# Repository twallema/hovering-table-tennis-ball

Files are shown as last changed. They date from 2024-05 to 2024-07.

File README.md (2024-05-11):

# Control Theory Hands-on Practical

## Hovering a table tennis ball at a fixed height

Dr. Tijs W. Alleman, Daniel Illana, Dr. Gauthier Vanhaelewyn

Correspondence: tijs.alleman@ugent.be 

BIOMATH, Department of Data Analysis and Mathematical Modelling, Ghent University, Coupure Links 653, Ghent, 9000, Belgium

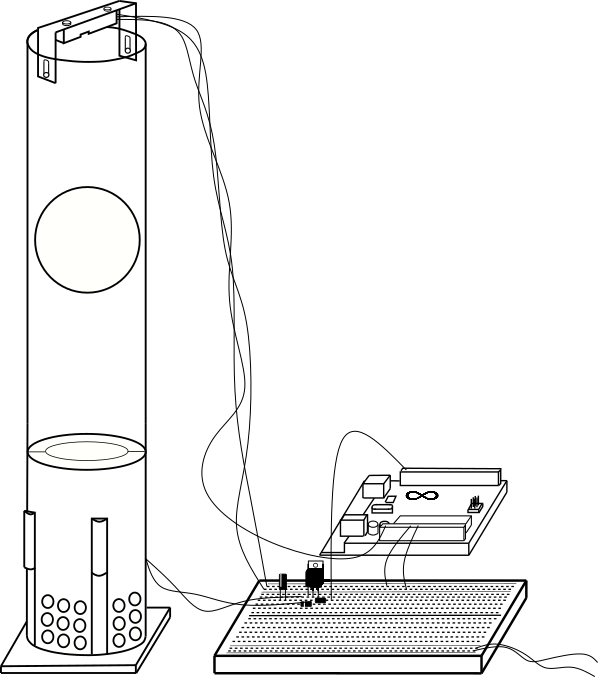
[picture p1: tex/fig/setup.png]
setup


### Aim

In this practical, we turn control theory into practice by hovering a table tennis ball at a fixed height in a transparent tube. We use an Arduino Uno to build a closed loop feedback controller. We measure the ball’s height using an infrared distance sensor at the top of the tube, which we the use to control a fan at the bottom of the tube. First, we study the setup’s open-loop behavior and gather response data to calibrate a mathematical model. We then use Matlab’s Simulink environment to perform an in-silico tuning of several closed-loop feedback controllers, such as the Proportional-Integral-Derivative (PID) controller and Linear-Quadratic Regulator (LQR) state feedback controller. Finally, the performance of the tuned controllers is examined and compared using the experimental setup. This setup serves as an intuitive and visual test bed for the closed-loop feedback controllers introduced in the theoretical course. Our aim is to introduce students to the use of electronics, the unfortunate reality of noisy sensors and dead time, along with their implications on closed-loop stability, the application of control theory to non-linear systems, and to the use of mathematical modeling to support the in-silico design of a suitable controller.

### Getting started

All relevant information is included in the practical notes. This repository contains all LaTex, Matlab, and Wolfram Mathematica code needed to replicate the results shown in the practical notes.

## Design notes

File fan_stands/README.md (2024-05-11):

# Fan stands

+ `FUFTICAILV80G0N.stl`: Original fan stand, retrieved from https://www.instructables.com/Float-a-Ping-Pong-Ball-at-Will/

+ `fan_stand_short.stl`: Modified fan stand. Modification of `FUFTICAILV80G0N.stl` so transparent polycarbonate tube can fit inside the fan stand. By Ben de Saveur. Has not been 3D printed and tested (11/05/2024).

+ `fan_stand_long.stl`: Modified fan stand. Elongation of `fan_stand_short.stl`, in order to have more distance between the fan and the ball, which will likely minimise lift-off dead time.  By Ben de Saveur. Has not been 3D printed and tested (11/05/2024).

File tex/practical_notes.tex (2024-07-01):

\documentclass[10pt,twoside,openright]{article}

%---------------------------------------------------------------------------
%List of packages with theid respective use, you can uncomment if not used
%---------------------------------------------------------------------------

%--------------layout of the document--------------
% this package is used to get a wider A4 paper
\usepackage{a4wide}
% these packages are used to produce nicer captions
\usepackage[font={small},labelfont={bf,sf},width=0.8\textwidth, singlelinecheck=false]{caption}
%\usepackage[font={small},labelfont={bf,sf},hang,singlelinecheck=false]{caption}
% use the titlesec package to change the section 
\usepackage[calcwidth,newparttoc]{titlesec}
% use the titletoc package to change the toc
\usepackage{titletoc}
% hyperrefs used in the produced pdf file
\usepackage[a4paper,plainpages=false]{hyperref}
% this package is used for colored text
\usepackage{xcolor}
%\usepackage[cmyk]{xcolor}
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
%http://anthony.liekens.net/index.php/LaTeX/SubscriptAndSuperscriptInTextMode
\newcommand{\superscript}[1]{\ensuremath{^{\textrm{#1}}}} 
\newcommand{\subscript}[1]{\ensuremath{_{\textrm{#1}}}}
% new commands to create nicer sub and superscripts in math mode
\newcommand{\sms}[1]{\mbox{\tiny{#1}}}
\newcommand{\lss}[1]{_{\mbox{\tiny{#1}}}}
\newcommand{\uss}[1]{^{\mbox{\tiny{#1}}}}

%---------------------------------------------------------------------------
% Short version commando to introduce figures. 
%---------------------------------------------------------------------------
%\mijnfiguur[H]{width=5cm}{bestandsnaam}{Het bijschrift bij deze figuur}{label}
\newcommand{\mijnfiguur}[5][ht]{            % Het eerste argument is standaar `ht'.
    \begin{figure}[#1]                      % Beginnen van de figure omgeving
        \begin{center}                      % Beginnen van de center omgeving
                    % Het eigenlijk invoegen van de figuur (2: opties, 3: bestandsnaam)
        \end{center}
        \caption{#4\label{#5}}          % Het bijschrift (argument 4) en het label (argument 3)
    \end{figure}
    }

%-----------------------------------------------------------------------------------------
% PDF properties (you only see this as document properties (metadata) of your pdf-document
%-----------------------------------------------------------------------------------------
\hypersetup{
    pdfauthor = {Your name},
    pdftitle = {Your title},
    pdfkeywords = {some relevant keywords}}

\setcounter{MaxMatrixCols}{20}

\usepackage{tcolorbox}
\usepackage{lipsum}
\usepackage{verbatim}

%path to graphics
\graphicspath{{fig/}}

%-------------------------------
% Opgave / Oplossing environment
%-------------------------------

\usepackage[framemethod=TikZ]{mdframed}
\mdfdefinestyle{warning}{%
	linecolor=white,
	align=center,
	roundcorner=3pt,
	innertopmargin=6pt,
	innerbottommargin=5pt,
	innerrightmargin=10pt,
	innerleftmargin=10pt,
	backgroundcolor=black!12,
	skipabove=0.4\baselineskip
}

\newcounter{opgave}[section]\setcounter{opgave}{0}
\renewcommand{\theopgave}{\arabic{section}.\arabic{opgave}}
\newenvironment{opgave}[2][]{%
	\refstepcounter{opgave}
	\label{#2}
	\mdfsetup{%
		frametitle={%
			\tikz[baseline=(current bounding box.east),outer sep=0pt]
			\node[anchor=east,rectangle,fill=gray!40]
			{\strut Exercise~\theopgave:~#1};}%
	}
	\mdfsetup{%
		innertopmargin=10pt,linecolor=white!30,%
		linewidth=0pt,topline=true,%
		frametitleaboveskip=\dimexpr-\ht\strutbox\relax%
	}

	\begin{mdframed}[]\relax}{%
\end{mdframed}}

\newenvironment{oplossing}[2][]{%
	\mdfsetup{%
		frametitle={%
			\tikz[baseline=(current bounding box.east),outer sep=0pt]
			\node[anchor=east,rectangle,fill=gray!20]
			{\strut Solution};}%
	}
	\mdfsetup{%
		innertopmargin=10pt,linecolor=white!30,
		linewidth=0pt,topline=true,%
		frametitleaboveskip=\dimexpr-\ht\strutbox\relax%
	}
	
	\begin{mdframed}[]\relax}{%
\end{mdframed}}

% ------------------
% Leeg vak
% ------------------

\newlength{\lvaklength}

\newcommand{\leegvak}[2]{\noindent\framebox[#1]{\parbox{#1}{\vspace{#2}}}}
\newcommand{\leegvakf}[1]{
\setlength{\lvaklength}{0cm}
\addtolength{\lvaklength}{0.925\textwidth}
%\addtolength{\lvaklength}{-\leftmargin}
\leegvak{\lvaklength}{#1}
}

\newcommand{\leegvakg}[1]{
\setlength{\lvaklength}{0cm}
\addtolength{\lvaklength}{0.875\textwidth}
%\addtolength{\lvaklength}{-\leftmargin}
\leegvak{\lvaklength}{#1}
}

\newcommand{\solbox}[2]{
\noindent\framebox[0.925\textwidth]{
\parbox{#1}{\vspace{#1}}
\begin{minipage}[c][#1][c]{0.925\textwidth}
	\centering
	#2
\end{minipage}
}}

%---------------------------------------------------------------------------
%---------------------------------------------------------------------------
% The actual document starts here
%---------------------------------------------------------------------------
%---------------------------------------------------------------------------
\begin{document}

\title{%
  Control Theory Hands-on Practical \\
  \Large Hovering a table tennis ball at a fixed height}
  
\author{Dr.~Tijs W. Alleman$^{1,2,*}$, Daniel Illana$^{1}$, Dr.~Gauthier Vanhaelewyn$^{1}$, Dr.~Elena Torfs$^{1,3}$}
\maketitle

$^*$Correspondence: \url{tijs.alleman@ugent.be} \\
$^1$BIOMATH, Department of Data Analysis and Mathematical Modelling, Ghent University\\
$^2$Infectious Disease Dynamics Group, Department of International Health, Johns Hopkins University Bloomberg School of Public Health\\
$^3$modelEAU, Department of Civil Engineering and Water Engineering, Universit\'e Laval\\
Available on GitHub: \url{https://github.com/twallema/hovering-table-tennis-ball}\\

\begin{center}

\end{center}

\paragraph{Aim} In this practical, we turn control theory into practice by hovering a table tennis ball at a fixed height in a transparent tube. We use an Arduino Uno to build a closed loop feedback controller. We measure the ball's height using an infrared distance sensor at the top of the tube, which we the use to control a fan at the bottom of the tube. First, we study the setup's open-loop behavior and gather response data to calibrate a mathematical model. We then use Matlab's Simulink environment to perform an in-silico tuning of several closed-loop feedback controllers, such as the Proportional-Integral-Derivative (PID) controller and Linear-Quadratic Regulator (LQR) state feedback controller. Finally, the performance of the tuned controllers is examined and compared using the experimental setup. This setup serves as an intuitive and visual test bed for the closed-loop feedback controllers introduced in the theoretical course. Our aim is to introduce students to the use of electronics, the unfortunate reality of noisy sensors and dead time, along with their implications on closed-loop stability, the application of control theory to non-linear systems, and to the use of mathematical modeling to support the in-silico design of a suitable controller.

\setcounter{tocdepth}{2}
\tableofcontents

\clearpage
\section{Introduction}

\subsection{Electronics}

To build the practical setup, we first need to familiarise ourselves with the bread and butter of electronics: the resistor, capacitor, diode and transistor. In this short intro we use the hydraulic circuit analogy, to explain some basic concepts. In this analogy, an electrical circuit is thought to be a hydraulic circuit consisting of pipes, valves, pumps, etc. Charge is represented by the water amount, voltage is represented by the water pressure, and current is represented by the water flow.

\paragraph{Resistor}
As the name implies, resistors add resistance to the circuit and reduce the flow of electrical current. In the hydraulical circuit analogy a resistance is represented by a throttling valve, or alternatively, as rocks in a river, hindering the flow of water. Resistors are typically represented as a pointy squiggle with a value next to it (Fig.~\ref{fig:resistor}). In electronic devices, resistors are used to avoid damage resulting from high currents. When building an electronic circuit, it is paramount to check the amount of current flowing through each analog component by using Ohm's law,
\begin{equation}
I = \frac{V}{R},
\label{eqn:Ohms law}
\end{equation}
where V is voltage in Volt (V), I is the electric current in Amps (A) and R is the resistance in Ohms ($\Omega$). Most electronic components, f.i. an LED, have little internal resistance. When applying even the smallest voltage directly to an LED, the LED will light up briefly and then shutdown forever. Generally speaking, overloading electronic circuits by mistake is common and not very dangerous. \textbf{In any case, when noticing the characteristic smell of a shortcircuit (a combination of ozone and burnt plastic) during this practical, please pull out the wall plug immediately!} During this practical we will use a 2.2 $k\Omega$ resistor to limit the current of a voltage sent from the Arduino Uno to a transistor.
\mijnfiguur[h!]{width=6cm}{resistor.jpg}{(upper) real life resistor. (lower) schematic representation of a transistor.}{fig:resistor}

\paragraph{Capacitor}
A capacitor is a component that stores electricity and then discharges it into the circuit when there is a drop in current. You can think of a capacitor as a water storage tank that releases water when there is a drought to ensure a steady stream. Therefore, capacitors are typically used to filter a noisy current. Further, capacitors are preferred over batteries in applications that require a rapid discharge, such as in a defibrillator. The values that you will typically encounter in most capacitors are measured in picofarad (pF), nanofarad (nF), and microfarad ($\mu F$). The most commonly encountered types of capacitors are ceramic disc capacitors that look like tiny M\&Ms with two wires sticking out of them and electrolytic capacitors that look more like small cylindrical tubes with two wires coming out the bottom (Fig.~\ref{fig:capacitor}). The main difference is that ceramic disc capacitors are non-polarized, meaning that electricity can pass through them no matter how they are inserted in the circuit. Opposed, electrolytic capacitors are polarized, meaning one leg needs to be connected to the ground side of the circuit and the other leg must be connected to power. For this practical we will be using a 22 $\mu F$ electrolytic capacitor as an analog filter for the power supply of the IR proximity sensor. \textbf{Because the provided capacitor is electrolytic, please make sure you respect its polarity.}

\mijnfiguur[h!]{width=7cm}{capacitor.jpg}{(left) real life ceramic capacitor and schematic representation (right) real life electrolytic capacitor and schematic representation.}{fig:capacitor}

%bron figuren: https://www.instructables.com/id/Basic-Electronics/

\paragraph{Diode}
A diode only allows electrical current to pass through them in one direction, its hydraulic analogy is a non-return valve. Diodes are useful to prevent electricity from flowing in the wrong direction. When the voltage applied to an electric DC motor is abruptly switched off, the fan will keep spinning for a short while. As such, the motor will act as a generator of current until its blades come to a standstill. Charge will build up on what was the negative terminal of the motor and this charge will want 'a way out'. Adding a diode in parallel with the motor provides a path for dissipation of stored energy when the voltage is cut. Similar to the electrolytic capacitor, the diode is polarised and the ring found on one end of the diode indicates the side of the diode which connects to ground. \textbf{When building the setup, please mind that the ring on the diode points in the right direction (Fig.~\ref{fig:fritzing}).}

\mijnfiguur[h!]{width=6cm}{diode.jpg}{(upper) real life diode (lower) schematic representation of a diode.}{fig:diode}
%\mijnfiguur[h!]{width=5cm}{flybackDiode.png}{The flyback diode allows charge to dissipate without arcing across the switch (analog component), or without flowing back to ground through the +5 V voltage supply.}{fig:flybackDiode}

\paragraph{Transistor} A transistor can act as a switch or gate for electronic signals, opening and closing many times per second. It typically has three pins: the base, emitter and collector pins (Fig.~\ref{fig:transistor}). A transistor uses a small electrical current at its base pin to control the current passing between its collector and emitter pins. The amount of current allowed to pass between the collector and emitter pins is proportional to the voltage being applied at the base pin. A transistor is therefore a good way of controlling a high voltage/high current circuit (fan motor, 12 VDC) using a low voltage/low current signal (Arduino, 5 VDC). An (inperfect) hydraulic analogy for a transistor is an adjustable valve. Passing current through a transistor costs energy and therefore observing a voltage drop of 1 V over a transistor is common. This energy is dissipated in heat so \textbf{transistors heat up to well over 100 \textdegree C under load. Never touch your transistor while operating the setup!}\\

\mijnfiguur[h!]{width=6cm}{BD537.jpg}{BD537 transistor used to control the fan's motor.}{fig:transistor}

%\begin{tcolorbox}[colback=white,colframe=black,title=\textbf{Takeaway lessons}]
%\begin{itemize}
%\itemsep0em 
%\item A limited number of analog components can be arranged to fulfill specific tasks. This is accomplished by designing the circuit so that the right current is provided to the right component.
%\item Analog components can be combined with programmable microcontrollers so that the amount of current flowing through each analog component can vary/be controlled. This allows to build more complex/interactive electronics.
%\end{itemize}
%\end{tcolorbox}

%bron: https://www.arduino.cc/en/guide/introduction, Arduino voor Dummies (John Nussey)

\subsection{The Arduino Uno Rev 3, its components and signals}

Using only resistors, capacitors, diodes and transistors, it is possible to build simple electronic devices that do a specific job, such as an egg timer or a security buzzer that goes off when you keep the fridge open too long. The behavior of such circuits is solely based on the chemical properties of the components, which need to be computed beforehand to make sure that the right amount of current is flowing through the right components. This makes these simple devices very good at their specific job, but they're limited in what they can do. The microcontroller, a tiny computer present on the Arduino Uno can be used can be used in conjunction with the aforementioned analog circuitry to allow for more advanced behavior. The amount of current flowing through the analog components is now variable and controlled, rather than constant and computed beforehand.\\

Arduino is an open-source electronics platform based on easy-to-use hardware and software. The Arduino hardware consists of a small circuit board containing a microcontroller chip and several connections (Fig.~\ref{fig:ARDUINO_UNO}), allowing us to read inputs such as light on a sensor, a finger on a button, or even a Twitter message - and turn them into an output - activating a motor, turning on an LED, publishing something online. This is accomplished by telling your board what to do when certain inputs are encountered by sending a set of instructions to the microcontroller on the board. To do so you can use the Arduino Software (IDE), as well as other programming languages such as Python and Matlab. In this practical, we'll program our Arduino Uno using the Matlab's Simulink environment. Let's examine the Arduino's components closer.

\paragraph{Microcontroller} You can think of the microcontroller chip itself as the \textit{brains} of the board. The chip used in the Arduino Uno is the ATmega328p, made by Atmel. It’s the large, black component in the center of the board. It’s actually not alone but rather sits in a socket. If you were to remove the microcontroller, it would look like the one shown in Figure \ref{fig:ATmega328p}.

\mijnfiguur[h!]{width=6cm}{ATmega328.jpg}{The brain of the Arduino Uno R3: the Atmel ATmega328p microcontroller.}{fig:ATmega328p}

\paragraph{Header sockets}
The microcontroller socket connects all 28 legs of the ATmega328 microcontroller chip to other sockets, referred to as header sockets, which have been arranged around the board and labeled for ease of use. They are the black sockets that go around the edge of the Arduino board. These are divided up into three main groups: digital pins, analog input pins, and power pins.  All these pins transfer a voltage, which can either be sent as output or
received as an input. These pins are important as they allow additional circuitry to be connected to the board quickly and easily.

\paragraph{Power pins} You use the power pins to distribute power to inputs and outputs wherever it’s needed (Fig.~\ref{fig:ARDUINO_UNO}). GND marks the ground pins, which are essential to complete circuits. There is also a third ground by pin 13. All these pins are linked and share the same \textit{common} ground. You can use the 5V and 3.3V pins to supply power to components or circuits. However, the Arduino can only supply about 40 mA of current without getting damaged. This is enough to power most sensors but not enough to power a larger motor. We'll thus have to supply the power for the blower fan externally.

\paragraph{Digital pins} Signals are defined as time-varying \textit{quantities} conveying information, typically a voltage. So when we talk about signals, just think of them as a voltage that's changing over time. You use the \textit{digital pins}, which run across the top of the board (Fig.~\ref{fig:ARDUINO_UNO}), to \textbf{send and receive} digital signals. Digital signals are made up of a sequence of \textit{bits}. A bit represents only one of two states: off or on, 0 or 1, or in electrical terms, 0V or 5V, but no values in between. The amount of information conveyed by a digital signal is characterised by its number of bits. On the Arduino Uno, a digital signal has 10 bits, giving rise to a total of 1024 possible outcomes, corresponding to a number between 0 and 1023. A temporal graph of a digital signal looks like a series of square waves (Fig.~\ref{fig:signals}). In practice, ten bits means the Arduino Uno and your computer are communicating by sending out ten equally long pulses of 0V or 5V within a set time interval. F.i. the computer will send the Arduino Uno a sequence of 10 bits (zeros or ones) in 1 millisecond, implying each bit is 0.100 milliseconds in length. Then there may be a small pause, say 1 millisecond, after which the Arduino Uno gets 1 millisecond to send the computer ten zeros or ones. These timings typically obey a certain protocol, used globally, such as HDMI and USB serial.

\paragraph{Analog pins} These pins are used to \textbf{receive} analog signals (Fig.~\ref{fig:ARDUINO_UNO}). The fundamental difference between an analog signal and a digital signal is that an analog signal is continuous and can assume all values between 0V or 5V (Fig.~\ref{fig:signals}). However, when receiving a voltage between 0 V and 5 V at pin A0-A5, the voltage is automatically converted to a digital value by the Arduino's on-board analog-to-digital converter before it is sent to your computer. \textbf{Therefore, both analog and digital inputs are represented by a number between 0 and 1023 on your computer, and therefore the maximum resolution of any signal on an Arduino Uno is 1/1024}.

\mijnfiguur[h!]{width=9cm}{analog_digital_signal.pdf}{The fundamental difference between an analog and a digital signal. A continuous analog signal (left). A discrete 6-bit digital signal (right).}{fig:signals}

\paragraph{Pulse Width Modulation}
The very shrewd ones among you may have noticed that there seem to be \textbf{no pins for analog outputs}. In fact, there are, but they’re hidden among the digital pins marked as PWM using the “\textasciitilde” symbol. PWM stands for \textit{Pulse Width Modulation}, which is a technique you can use to mimic a continuous analog output using a discrete digital output. A digital output is either on or off but this can be done extremely quickly. If the output is on half the time and off half the time, it is described as having a 50 percent \textit{duty cycle}. Because it is blinking faster than the human eye can perceive, an LED pulsed using a 50 percent duty cycle looks as though it is at half brightness (Fig.~\ref{fig:PWM}). With a DC motor as an output, a 50 percent duty cycle has the effect of moving the motor at half speed. So in this case PWM allows you to control the speed of a motor by pulsing it at an extremely fast rate. PWM works best for devices with sufficient inertia such as electric motors and pumps.

\mijnfiguur[h!]{width=\textwidth}{PWM.pdf}{From left to right: A 20 \%, 70 \% and 90 \% PWM duty cycle.}{fig:PWM}

\mijnfiguur[h!]{width=16cm}{ARDUINO_UNO.png}{An actual Arduino Uno R3 (left) and a schematic highlighting the most important parts (right).}{fig:ARDUINO_UNO}

%\newpage
%\phantom{hello}

%\begin{tcolorbox}[colback=white,colframe=black,title=\textbf{Takeaway lessons}]
%\begin{itemize}
%\itemsep0em 
%\item A signal is a voltage changing over time.
%\item Analog signals are continuous and can assume any voltage between 0 V and 5 V on the Arduino Uno.
%\item Digital signals are discrete and can only assume 0 V or 5 V, corresponding to zeros and ones. Digital signals are characterised by their number of bits and protocols such as USB serial are needed to allow efficient communication.
%\item Analog signals can be mimicked using a digital signal and this is called \textit{Pulse Width Modulation}.
%\end{itemize}
%\end{tcolorbox}

\section{Practical setup}

\subsection{Materials}

\begin{itemize}
\itemsep0em 
\item Arduino Uno R3
\item Male-male jumper wires
\item Solderless breadboard
\item Sharp 2Y0A21 IR proximity sensor
\item 2.2 $\text{k}\Omega$ resistor
\item BD139 or BD537 transistor
\item Diode
\item 22 $\mu\text{F}$ electrolytic capacitor
\item Sunon 40x40x10 mm 5~VDC blower fan
\item Fan stand, obtained from \url{https://www.instructables.com/Float-a-Ping-Pong-Ball-at-Will}
\item 12~ VDC power supply
\item Transparent polycarbonate tube, 65 cm long
\item USB-A to USB-B cable
\item Table tennis ball
\end{itemize}

\begin{figure}[h!]
\centering

\caption{Schematic of the practical setup.}
\end{figure}

\subsection{Electronic circuit}
The electronic circuit diagram depicted in Fig.~\ref{fig:circuit} is built on a solderless breadboard (Figs.~\ref{fig:breadboard},~\ref{fig:fritzing}). A solderless breadboard consists of two halves split by the center divider and are electrically independent. Each half consists of roughly 50 terminal strips (5 hole columns) and two power rails. The power rails are horizontally connected over the full length of the breadboard, while each terminal strip is vertically connected. There is no vertical connection between the power rails and no horizontal connection between the terminal strips.\\

\mijnfiguur[h!]{width=9cm}{breadboard.pdf}{A solderless breadboard. The power rails are horizontally connected, while the terminal strips are vertically connected.}{fig:breadboard}

The electronic circuit diagram depicted in Fig.~\ref{fig:circuit} can be broken down to two seperate parts: 1) A circuit for the IR proximity sensor, and 2) A transistor circuit to control the fan speed. The IR proximity sensor has 3 pins, a ground (GND) pin, a supply voltage ($\text{V}_{\text{CC}}$) pin and an output voltage ($\text{V}_{0}$) pin. We supply the sensor with 5 VDC power drawn from the Arduino Uno. As its output $\text{V}_{0}$, the sensor returns a voltage between 0~VDC and 5~VDC, either unfiltered to the Arduino's analog input pin (A0), or filtered via an RC filter, as illustrated in Fig.~\ref{fig:fritzing}. An RC filter is an analog first-order low-pass filter, attenuating high-frequency noise on the sensor's output voltage. Using a resistor of $R=22~k\Omega$ and a capacitor of $F=2.2~\mu F$ yields an RC filter with a time constant of $\tau = R*C = 0.1~s$,
\begin{equation}
H(s) = \frac{1}{RC s + 1} = \frac{1}{0.1s + 1}.
\end{equation}

The transistor circuit used to drive the fan's motor combines two concepts from the introduction: a transistor controlled using Pulse Width Modulation (PWM) and a flyback diode. To power the motor, we need to send 12~VDC through it and then on to ground. To give the Arduino Uno control of the motor’s power, you use a transistor, which functions as an electrically operated switch activated by means of PWM from your Arduino’s digital pins. The emitter of the transistor is connected to common ground and the collector is connected to the motor. To control the flow between the emitter and collector, a low power PWM signal can supplied at the base pin (Fig.~\ref{fig:transistor}). You connect pin D9, which has PWM capabilities, to the base pin of the transistor and use a 2.2 $k \Omega$ resistor to limit the current. To limit the chances of a creating a reverse current after cutting the motor's power, we place a flyback diode parallel across the motor. The practical implementation of the motor's electronic circuit on the solderless breadboard is shown in Fig.~\ref{fig:fritzing}. Note how the grounds from both power rails on the solderless breadboard and the Arduino Uno are shared, which is essential to making this setup work.

\subsection{Coupling the Arduino to MATLAB}
Make sure the \texttt{Arduino support package for Simulink} is installed locally on the computers that will be used (Simulink $>$ \texttt{APPS} $>$ \texttt{Get Add-Ons} $>$ \texttt{Get Hardware Support Packages} $>$ \texttt{Simulink Support Package for Arduino}). Connect the Arduino to the computer with the USB cable. Select \texttt{MODELLING} > \texttt{Model Settings} > \texttt{Hardware Implementation} > \texttt{Hardware board: Arduino Uno} to reveal the \texttt{HARDWARE} tab. To run a Simulink model on your Arduino board, select \texttt{HARDWARE} > \texttt{Run with IO}. To execute code continuously on your Arduino, set the simulation time to \texttt{inf}.

\begin{landscape}
\mijnfiguur[h!]{scale=1.4}{circuit.pdf}{Electronic circuit diagram. Note how the IR sensor circuit and the transistor circuit are two seperate entities.}{fig:circuit}
\end{landscape}

\begin{landscape}
\mijnfiguur[h!]{scale=0.8}{levitatingPingPongCircuit_bb.pdf}{Electronic circuit built on the solderles breadboard.}{fig:fritzing}
\end{landscape}

\subsection{Calibrating the IR proximity sensor}
The relationship between the IR sensor's output voltage and its distance to the table tennis ball is needed. First, we collected data by hovering the ball at several heights (using a PID controller) and recording the sensor's output voltage (Fig.~\ref{fig:sensor_calibration}). We then expiremented with several mathematical relationships and found the following \textit{logit} relationship adequately described the ball's height in function of the recorded voltage,
\begin{equation}\label{eq:calibration_sensor}
H(V) = H_{\text{max}} + \dfrac{1}{\beta} \left[ \ln \left( \dfrac{V_{\text{max}} - V_{\text{min}}}{V_{\text{max}} - V} - 1 \right) - \ln(\alpha) \right]
\end{equation}
with $H_{\text{max}} = 0.65~m$, $\alpha = 2.19$, $\beta = 8.91$, $V_{\text{min}} = 0.70~V$, $V_{\text{max}} = 4.51~V$. At the bottom of the tube, a change in the ball's height results only in a very small change in the sensor's recorded voltage. Due to the noise on the recorded voltage, measuring height differences in the bottom 20~cm of the tube is difficult. As the ball gets close to the IR proximity sensor, above 58~cm, the sensor's output voltage drops back to 2~V.

\mijnfiguur[h!]{width=\linewidth}{calibration_sensor.pdf}{Relationship between the height of the table tennis ball and the IR sensor's output voltage.}{fig:sensor_calibration}

\subsection{Mathematical model}

\subsubsection{Model structure}\label{section:model_structure}
The fan at the bottom of the tube blows air upwards around the table tennis ball, which hampers the flow of air thereby creating an upwards \textit{drag force} proportional to the square of the relative velocity of the ball (Fig~\ref{fig:ballInTube}). Air molecules hitting the bottom of the ball are slowed down and subsequently deflected around the ball, resulting in the formation of a high pressure region. The incoming laminar airflow will adhere to the surface of the ball\footnote{This is called the \textit{coanda effect} which you may have know as the deflection of a vertical stream of water across the back of a spoon.} up until the \textit{separation point} where the formation of turbulent eddies begins. In the wake of the ball, a turbulent region of low pressure forms and it is the pressure difference between the bottom and top of the ball that generates the drag force. Opposed is the force of gravity, which pulls the ball down with a constant force irregardless of the ball's velocity. The total force exerted on the tennis ball along the $z$ axis is therefore equal to,
\begin{equation}\label{eq:pingPongForce}
F = \frac{1}{2} \rho A C_D v_{\text{rel}}^2 - mg,
\end{equation}
where $\rho_{\text{air}}$ is the density of air, equal to 1.225 $kg \cdot m^{\text{-}3}$. A is the surface area of the table tennis ball, equal to $4\pi r^2$ with a radius $r=0.02~m$. $C_D$ is the coefficient of drag, which is 0.47 (-) for Reynolds numbers below $Re<10^5$ (S.~Hoerner, 1965. Fluid-Dynamic Drag). $m$ is the mass of the ping ball and is equal to $0.00283~kg$. g is earth's gravitational constant equal to 9.81 $m \cdot s^{\text{-}2}$. $v_{\text{rel}}$ is the relative velocity of air around the table tennis ball in $m \cdot s^{\text{-}1}$, which depends on the velocity of the airflow inside the tube ($v_{\text{air}}$), as well as on the velocity of the table tennis ball itself ($v_{\text{ball}}$). However, because the velocity of the airflow in the tube is not known exactly we make two assumptions. First, we assume it is related to the PWM signal used to control the fan's speed by means of a power law function. Second, we assume there is no pressure drop along the length of the tube, and hence, the air's speed is independent of the position in the tube (Excercise~3.1). Mathematically,
\begin{equation}\label{eq:assumption_no_pressure_drop}
v_{\text{rel}} = v_{\text{air}} - v_{\text{ball}} = \alpha u(t)^\beta - v_{\text{ball}},
\end{equation}
where $\alpha~(m \cdot s^{\text{-}1})$ and $\beta~(-)$ are parameters of the power law function and $u(t)$ is the value of the PWM signal, located between 0 and 255, and corresponding to a 0 \% and a 100 \% duty respectively. Hence, we can rewrite Eq.~\ref{eq:pingPongForce} as follows,
\begin{equation}\label{eq:pingPongForceExtended}
F = \frac{1}{2} \rho A C_D \left( \alpha u(t)^\beta- v_{\text{ball}} \right)^2 - mg.
\end{equation}
Using Newton's second law of motion, we arrive at the following non-linear second order ODE describing the ball's movement inside the tube,
\begin{equation}\label{eq:ODEmodel}
m \frac{\text{d}^2 z}{\text{d}t^2} = \frac{1}{2} \rho A C_D \left(\alpha u(t)^\beta - \frac{\text{d}z}{\text{d}t}\right)^2 - m g.
\end{equation}
Next, as is common practice in control theory, we rewrite the mathematical model in a state-space representation. The system's states, denoted $\bm{x}$, are the position $z$ and velocity $v$ of the ball. Its only observed output $y$ is the position of the ball $z$, its only input is $u(t)$. By substituting $v = dz /dt$ in Eq.~\ref{eq:ODEmodel}, we arrive at the following non-linear model in state-space representation,
\begin{equation}\label{eq:pingPongModelStates}
\begin{cases}
\bm{\dot{x}}(t) &= \bm{f}\big(\bm{x(t)},~u(t)\big) = \begin{bmatrix} \dot{z}(t) \\ \dot{v}(t) \end{bmatrix} = \begin{bmatrix} v(t) \\ \dfrac{\rho A C_D}{2 m} (\alpha u(t)^\beta - v(t))^2 - g \end{bmatrix},\\
y(t) &= g\big(\bm{x(t)},~u(t)\big) = z(t).
\end{cases}
\end{equation}

\mijnfiguur[t!]{width=0.65\textwidth}{force_diagram.pdf}{(left) Velocity contours of the flow around a smooth sphere placed in a laminar fluid flow. (right) Forces acting upon the sphere.}{fig:ballInTube}

\subsubsection{Equilibrium and operating points}

\paragraph{Equillibrium points} A system is in equillibrium when the derivatives of all states are zero when no input is provided, mathematically, $\bm{\dot{x}}(t) = \bm{f}(\bm{x(t)},~ 0) = 0$. Substitution in Eq.~\ref{eq:pingPongModelStates} yields the following conditions,
\begin{equation}
\begin{cases}
v^* = 0~m \cdot s^{\text{-}1}, \\
g = 0~m \cdot s^{\text{-}2},
\end{cases}
\end{equation}
and there is no condition on the ball's position $z$. Thus, the ball can only be at rest at any point in the tube with the fan switched off in the abscence of gravity. Therefore, on earth, where $g = 9.81~m \cdot s^{\text{-}2}$, the system does not have an equillibrium point. In practice, when the fan is switched off, the ball will be in equillibrium at the bottom of the tube, where its weight is supported by the fan stand.

\paragraph{Operating points} A system is in an operating point when the derivatives of all states are zero when input is provided, mathematically, $\bm{\dot{x}}(t) = \bm{f}\left(\bm{x(t)},~\bar{u}\right) = 0$. Substitution of this condition in Eq.~\ref{eq:pingPongModelStates} yields,
\begin{equation}\label{eq:operating_point}
\begin{cases}
v^* = 0~m \cdot s^{\text{-}1}, \\
\bar{u} = \left(\dfrac{2 m g}{\rho A C_D \alpha^2}\right)^{\dfrac{1}{2 \beta}}.
\end{cases}
\end{equation}
From which we conclude: 1) Any position inside the tube can be an operating point as there is no condition on the ball's position $z$, 2) the ball hovers in an operating point because $v^*=0~m \cdot s$, and 3) the fan speed needed to hover the ball $\bar{u}$ only depends on system parameters. Therefore, there exists one unique fan velocity given by Eq.~\ref{eq:operating_point} that will make the ball hover at a fixed height in the tube, irregardless of the ball's position in the tube. When designing a controller, the aim is to stabilise a desired operating point $(z^*,~0,~\bar{u})$.

\subsubsection{Stability of the operating points}\label{section:stability}
To examine the stability of the operating points of a non-linear system analytically, we first linearize the system and evaluate it at generic point $(\bm{x^*}, u^*) = (z^*, v^*, u^*)$. A linear state-space system has the following form,
\begin{equation}
\begin{cases}
\bm{\dot{x}}(t) &= \bm{A} \bm{x}(t) + \bm{B} u(t), \\
y(t) &= \bm{C} \bm{x}(t) + D u(t),
\end{cases}
\end{equation}
Linearising a non-linear system is done by means of a first-order Taylor approximation in the operating point,
\begin{equation}
\bm{A} = \left. \dfrac{\partial \bm{f}}{\partial \bm{x^T}}\right|_{(z^*, v^*, u^*)} ~ \bm{B} = \left. \dfrac{\partial \bm{f}}{\partial u}\right|_{(z^*, v^*,u^*)} ~ \bm{C} = \left. \dfrac{\partial g}{\partial \bm{x^T}}\right|_{(z^*, v^*, u^*)} ~ \bm{D} = \left. \dfrac{\partial g}{\partial u}\right|_{(z^*, v^*, u^*)}.
\end{equation}
Applied to Eq.~\ref{eq:pingPongModelStates},
\begin{equation}\label{eq:linearised_system}
\begin{cases}
\bm{\dot{x}}(t) &=
\underbrace{
\begin{bmatrix}
0 & 1 \\
0 & \dfrac{\rho A C_D}{m} \left( v^* - \alpha \left( u^* \right)^\beta \right)
\end{bmatrix}}_{\bm{A}}
\begin{bmatrix}
z(t) \\
v(t)
\end{bmatrix}
+
\underbrace{
\begin{bmatrix}
0 \\
\dfrac{\alpha \beta \rho A C_D}{m} (u^*)^{\beta-1} \left(\alpha (u^*)^\beta - v^* \right)
\end{bmatrix}}_{\bm{B}}
u(t), \\
y(t) &=
\underbrace{
\begin{bmatrix}
1 & 0
\end{bmatrix}}_{\bm{C}}
\begin{bmatrix}
z(t) \\
v(t)
\end{bmatrix}
+
\underbrace{0}_{D} u(t), \\
\end{cases}
\end{equation}
where $\bm{A}$ is the \textit{system matrix}, $\bm{B}$ is the \textit{input matrix}, $\bm{C}$ is the \textit{output matrix} and $D$ is the \textit{feedthrough matrix}. The eigenvalues of the matrix $\bm{A}$ at the operating point $(z^*,~0,~ \bar{u})$ determine its stability and are found by solving its characteristic equation,
\begin{equation}
\text{det}\left( \lambda I - A \right) = 
\begin{vmatrix}
\lambda & -1 \\
0 & \lambda + \dfrac{\rho A C_D}{m}  \alpha \bar{u}^\beta
\end{vmatrix}
= 0
\end{equation}
\begin{equation}\label{eq:linearised_system_poles}
\iff \lambda_1 = 0\ \lor\ \lambda_2 = - \dfrac{\rho A C_D}{m} \alpha \bar{u}^\beta.
\end{equation}
If all real parts of the eigenvalues are negative than the system is \textit{asymptotically stable} and if at least one real part is positive and the others negative, the system is \textit{unstable}. For $\alpha>0$, our system has one negative eigenvalue and one zero eigenvalue, and therefore exerts \textit{marginal or neutral stability}, which is between an asymptotically stable and an unstable system. When displaced by the fan, the ball will not return to a common steady state, nor will it go away without limit. To examine the system's stability,we can alternatively write down the linearised system's transfer function and examine its poles in the operating points,
\begin{equation}
H(s) = \bm{C} (s \bm{I} - \bm{A})^{\text{-}1} \bm{B} + \bm{D},
\end{equation}
applied to Eq.~\ref{eq:linearised_system},
\begin{equation}
H(s) = \dfrac{\nicefrac{\alpha \beta \rho A C_D}{m}}{s \left(s - \nicefrac{\rho A C_D}{m} \left(v^* - \alpha (u^*)^\beta\right) \right)},
\end{equation}
whose poles in the operating point $(z^*,~ 0,~ \bar{u})$ are identical to those found by solving the characteristic equation (Eq.~\ref{eq:linearised_system_poles}). In Fig.~\ref{fig:streamPlots}, the phase trajectories of the system are given for three fan velocities, below ($u^* = 131$), at ($\bar{u} = 151$), and above ($u^* = 171$) the unique fan speed needed to hover the ball (Eq.~\ref{eq:operating_point})\footnote{For the calibrated values $\alpha = 0.19$ and $\beta = 0.63$, see Excercise~3.5.}. If a point ($z$, $v$) in the phase trajectory is chosen as the initial condition of the system, then the streamlines indicate the change in position and velocity of the table tennis ball over time. With an insufficient fan speed to hover the ball, any initial combination of position and velocity results in the ball landing at the bottom of the tube. Opposed, at a fan speed above the hovering speed, the ball always ends up at the top of the tube. Starting from any initial velocity, a fan speed of $u = 151$ guarantees the ball will eventually come to a standstill.

\mijnfiguur[h!]{width=\textwidth}{streamPlots.pdf}{Phase trajectories for three different values of the fan speed $u(t)$.}{fig:streamPlots}

\subsubsection{Controllability and observability}\label{section:controllability}

\paragraph{Controllability} The controllability matrix of the linearised system in an operating point $(z^*, 0, \bar{u})$ is computed as follows,
\begin{equation}\label{eq:controllability}
\bm{P}
=
\begin{bmatrix}
\bm{B} & \bm{AB}
\end{bmatrix}
=
\bar{u}^{\left(2\beta-1\right)} \dfrac{\alpha^2 \beta \rho A C_D}{m}
\begin{bmatrix}
0 & 1 \\
1 & - \dfrac{\alpha \rho A C_D}{m} \bar{u}^\beta \\
\end{bmatrix},
\end{equation}
and its rank is equal to the number of states (2). Therefore, the system is controllable, meaning an appropriate choice of fan speeds $u(t)$ can be used drive the ball from any initial state to any desired state within a finite timeframe.

\paragraph{Observability} The observability matrix of the linearised system is computed as follows,
\begin{equation}\label{eq:observability}
\bm{S}
=
\begin{bmatrix}
\bm{C} \\
\bm{CA}
\end{bmatrix}
= 
\begin{bmatrix}
1 & 0 \\
0 & 1
\end{bmatrix},
\end{equation}
and its rank is equal to the number of states (2). The system is therefore observable meaning the IR proximity sensor's measurement of the ball's position can be used in conjunction with a Luenberger state estimator to estimate the velocity of the ball. Hence, the system's known states can be used to estimate it's unknown states.

\section{Hands-on practical}

\subsection*{Overview of the practical}
This hands-on practical consists of four parts. In the first part you will study the physical system by analysing its \textbf{open-loop response} or how it reacts without a feedback controller. This will allow you to assess how the system reacts to inputs by the fan, assess the stability of operating points (Section~\ref{section:stability}). Further, you will learn how to filter the IR proximity sensor's signals. Finally, you will perform several response experiments, which you will then use to \textbf{calibrate the mathematical model of the setup} (Eq.~\ref{eq:pingPongModelStates}). In the second part of the practical, you will use the calibrated mathematical model to perform an in-silico tuning of a PID controller. In addition, you will tune a PID controller by means of the Cohen-Coon and Ziegler-Nichols \textbf{empirical tuning methods}. In the third part of this practicum, you will test the tuned PID controllers on the real system. You will study the \textbf{closed-loop response} of the system by studying the controller's P, I and D contributions more closely. You will further study the implications of dead time on the fan's response and measurement noise on the performance of the controller. The fourth and final part of the practical will introduce you to the design of the more advanced \textbf{Linear Quadractic Regulator} with \textbf{Luenberger estimator}. Its performance as compared to the PID controller will be assessed.

\subsection*{Part I: Open-loop control, time- and frequency response}

\subsection{Open-loop control of the fan's speed}
Before implementing any form of feedback control, we investigate how to control the system manually (open-loop control). We'll use the Simulink model shown in Fig.~\ref{fig:sendPWM} to control the fan speed. The model contains a \texttt{Knob} whose output is connected to a \texttt{Constant} block. The knob's output is limited to the interval 0-255 and represents the fan's motor speed $u_{\text{PWM}}$. Setting $u_{\text{PWM}}$ to 0 results in $0/255 \cdot 12\ \text{V} = 0$ V applied to the fan motor, while setting $u_{\text{PWM}}$ to 255 results in $255/255 \cdot 12\ \text{V} = 12$ V applied to the fan motor. A \texttt{display} block is used to more accurately show the value selected on the knob.\\

\pagebreak

\begin{opgave}[Open-loop control of the fan's speed]{}

\begin{enumerate}

	\item Implement the model in Simulink (Fig.~\ref{fig:sendPWM}) or open \textbf{writePWM.slx}. 
	
	\item Start by turning the knob to $u_{\text{PWM}} \approx 180$. Run the Simulink model by pressing the \texttt{Run with IO} button in the \texttt{Hardware} tab. Pay attention to the system's response. What is the minimum value $u_{\text{PWM}}$ needed to raise the ping pong ball from the stand?

		\leegvakf{1cm}

	\item What is the approximate $u_{\text{PWM}}$ needed to hover the table tennis ball at 30 cm?

		\leegvakf{1cm}

	\item What is the approximate $u_{\text{PWM}}$ needed to hover the table tennis ball at 50 cm? Are your findings in line with those obtained by analytically assessing the stability of the operating points (Section~\ref{section:stability})?

		\leegvakf{1cm}
	
\end{enumerate}

\end{opgave}

\mijnfiguur[h!]{scale=0.6}{sendPWM.pdf}{Simulink model used to control the fan speed.}{fig:sendPWM}

\subsection{Measuring and filtering the IR sensor's signal}
Next, we will measure the step response of the system. For this purpose, you can use the Simulink model \textbf{readProximity.slx} (Fig.~\ref{fig:readProximity}). An \texttt{analog read} block is used to read the sensor's output voltage at pin A0. However, the voltage was already transformed into a 10 bit digital signal by the Arduinos on-board analog-to-digital converter so a number between 0 and 1023 is returned. 
After changing the signal's datatype to \texttt{double}, we convert it back to a voltage between 0~V and 5~V. Next, the signal is smoothed by combining a \texttt{median filter} and a first-order system (low-pass filter). Next, Eq.~\ref{eq:calibration_sensor} is used to convert the voltage into a distance from the IR sensor (Fig~\ref{fig:sensor_calibration}). However, because of a singularity in Eq.~\ref{} at 0.70~V, the voltage is limited to a minimum of 0.701~V.  Finally, distance from the sensor is converted to height in the tube and a \texttt{saturation} block is used limit the height to a physcially plausible range.\\

\begin{opgave}[Measurement of the ping pong ball's height]{}

\begin{enumerate}
	\item Implement the model in Simulink (Fig.~\ref{fig:readProximity}) or open \textbf{readProximity.slx}.
	\item Manually control the height of the ping pong ball while observing the height using the \texttt{Scope}. How is the overall signal quality? Does  the signal quality differ at different heights? What could you do to improve this signal?
	
	\leegvakf{1cm}

\end{enumerate}
\end{opgave}

\begin{opgave}[Filtering the IR sensor's signal]{}

\begin{enumerate}
	\item Add a first-order transfer function after the block converting the voltage to the range 0-5~VDC. Set the gain to $K=1$ and time constant to $\tau = 0.2~s$. Optionally connect the time constant to a \texttt{knob} for convenience. Visualise the filtered and unfiltered signal using a \texttt{scope}. Manually control the height of the ping pong ball while observing the height using the scope. How is the signal quality now?
	
	\leegvakf{1cm}
	
	\item Vary the first-order transfer function's time constant. How does the signal quality change? How does the timing of the filtered signal differ from the unfiltered signal? Find an appropriate time constant to use for the rest of the practical.
	
	\leegvakf{2cm}
	
	\item What is the name of such a filter? Can you explain how this filter works?
	
	\leegvakf{2cm}
	
\end{enumerate}

\end{opgave}

\mijnfiguur[h!]{width=\linewidth}{readProximity.pdf}{Simulink model used to read the ball's height in open-loop control.}{fig:readProximity}

\subsection{Collecting time response data}

Having a mathematical model of the system is usefull to design a well-functioning controller. We previously derived a set of non-linear second-order ordinary differential equations representing the physical processes underlying the table tennis ball movement (Eq.~\ref{eq:pingPongModelStates}). This model, based on a combination of physical laws and unknown parameters is a \textbf{grey box model}. In practice, systems are often too complex to come up with a grey or white box model. Many complex, non-linear system's dynamics are reasonably approximated by linear models under typical operating conditions. However, our system, with its neutral stability, is not well approximated by a first- or second order transfer function and hence, no such model is identified during this practical. \\

You will perform experiments and use them to calibrate the unknown parameters $\alpha$ and $\beta$ in Eq.~\ref{eq:pingPongModelStates}. The first experiment is a \textbf{block-shaped response} experiment, which combines a step response experiment with a U-shaped response experiment (Fig.~\ref{fig:experiments}a). This experiment is preferred over the more simple step response experiment because it contains information on both the upward and downard trajectory of the table tennis ball, which differ from each other. Additionally, the U-shaped response contains information on the ball's \textbf{in-flight dead time} in response to changes in the fan speed. In the second \textbf{W-shaped response} experiment, a similar step-wise input is given, followed by a series of three step-wise changes in the fan speed, alternating below and above the fan speed needed to hover the ball $\bar{u}$(Eq.~\ref{eq:operating_point}) (Fig.~\ref{fig:experiments}b). The block-shaped response experiments will be used as \textbf{calibration dataset}, while the W-shaped response experiment will be used as a \textbf{validation dataset} to assess the predictive accuracy of our calibrated model. \\

\newpage
\begin{opgave}[Sytem response experiments]{}

	\begin{enumerate}
		\item Open the script \textbf{writeBlockResponse.m}, which is preprogramed to perform a step response, followed by a U-shaped response (Fig.~\ref{fig:experiments}a). The intial step response is performed by stepping the fan speed to $u_{\text{max}}$ for 7.5~s, followed by 7.5~s at the equillibrium fan speed $\bar{u}$ to stabilise the ball's spin for the second part of the experiment. Then, the U-shaped response is performed by stepping down the fan's speed to $u = \bar{u} - u_{\text{step}}$ for 2.5~s, then stabilising the ball at the equillibrium fan speed $\bar{u}$ for 5.0~s, followed by a 2.5~s step up to $u = \bar{u} + u_{\text{step}}$. By default, three initial step motor speeds $u_{\text{max}} = 170,~185,~255$, and two U-sizes $u_{\text{step}} = 6, 10$ are permutated, and every combination is performed in duplicate to average out natural variations in the response. Thus, a total of 12 experiments are performed. You will provide the observed time needed before the ball was lifted from the stand (\textit{lift-off dead time}), which is then automatically cut from the experiment. In the script, provide an accurate estimate of the fan's equillibrium speed \texttt{u\_eq} (Excercise~1), and set the \texttt{output\_name} to \textit{blockResponse.csv}. The script uses the Simulink model \textit{blockResponse.slx}. Limit the ball's height to 50~cm using a thin wooden stick.
		
		\item Open the script \textbf{writeWResponse.m}, which uses the Simulink model \textit{wResponse.slx} to log a W-shaped response experiment which we will use as a validation dataset (Fig.~\ref{fig:experiments}b). Five identical experiments are automatically performed to visualise the natural variation on the reponse. After all five experiments, you will provide one lift-off dead time which is then cut from the experiments. Use the automatically generated figure containing the fan speed and height response to \textbf{determine the in-flight dead time}.
		
			\fbox{%
  				\parbox{0.92\textwidth}{
   				$t_d$ =
  				}%
			}

	\end{enumerate}
	
\end{opgave}

\mijnfiguur[h!]{width=0.85\linewidth}{experiments.pdf}{(a) Fan speed and ball height during a block-shaped response experiment. (b) Fan speed and ball height during a W-response experiment.}{fig:experiments}

\subsection{Understanding the system's open-loop frequency response}
Finally, you will investigate the system's open-loop frequency response. You will do this by applying a sinusoidal input of varying frequency to the fan and observing the amplitude of the resulting sinusoidal changes in the ball's height, as well as the phase shift between the input and output signals. Using your observations, you construct an approximate \textbf{Bode diagram} allowing you to make further deductions on the system's dynamics. 

\begin{opgave}[Frequency response of the system]{}
	\begin{enumerate}
		\item  Open the Simulink model \textbf{frequency.slx} and use the \texttt{knob} to set the equillibrium fan speed needed to hover the ball, $\bar{u}_{\text{PWM}}$ (Excercise~3.1). Set the frequency knob to 10~rad/s, which results in the fan speed sinusoidally varying between $\bar{u}_{\text{PWM}} \pm 30$, within $t = \pi/10 = 0.3~s$ (= high-frequency input). Temporarily increase the value of $\bar{u}_{\text{PWM}}$ to overcome the additional energy needed to get the ball airborne. Next, hover the ball where the IR sensor's signal's quality is good, around 30~cm. Note that as the transistor heats up, its ability to pass a current increases. Hence, starting from a cold setup, you may need to initially use a value slightly higher than $\bar{u}_{\text{PWM}}$. What is the amplitude of the sinusoidal changes in the ball's height?
		
		\leegvakf{1cm}
		
		\item Decrease the frequency of the input signal to 1~rad/s in a step-wise manner. Prevent the ball from going fully down or up by making adjustments to $\bar{u}_{\text{PWM}}$. How does the amplitude of the ball's height change? Are the input and output signals in or out of phase?
		
		\leegvakf{1cm}
		
		\item Decrease the frequency of the input signal below 1~rad/s. Stop making temporary adjustments to $\bar{u}_{\text{PWM}}$ to prevent the ball from reaching either end of the tube. What is the amplitude of the ball's height? Not accounting for the dead time introduced by the initial energy needed to get the ball hovering, are the input and output signals in or out of phase?
		
		\leegvakf{1cm}
		
		\item Draw an approximate Bode diagram of the system. What kind of system is the Bode diagram characteristic of?
	\end{enumerate}
\end{opgave}

		\begin{figure}[t!]
			\centering
			
			
			\caption{Approximate Bode diagram based on the setup's open-loop frequency response.}
 		\end{figure}

\subsection*{Part II: System identification and PID controller tuning}

The second part of this practical can be done \textbf{independently from the lab set-up}. In this part of the practical, the unkown parameters in the mathematical model of the setup (Eq.~\ref{eq:pingPongModelStates}) are identified using the response data gathered in Excercise~3.4. Then, the calibrated mathematical model is implemented in Simulink and used to design a suitable PID controller \textbf{in-silico}. Finally, two \textbf{emperical tuning techniques}, by Cohen-Coon and Ziegler-Nichols, are used to tune a PID controller. 

\subsection{System Identification}

\begin{opgave}[Calibrating the mathematical model (Eq.~\ref{eq:pingPongModelStates})]{}

	\begin{enumerate}

		\item Use \textbf{systemIdentification.m} to calibrate the unkown parameters $\alpha$ and $\beta$ in Eq.~\ref{eq:pingPongModelStates} using the block-shaped response dataset gathered in Excercise~3.4.1. In the script, be sure to provide your estimate of the in-flight dead time (Excercise~3.4.2) and validate the paths to \textit{blockResponse.csv} and \textit{wResponse.csv}. The script will automatically minimize the sum-of-squared errors between the block-shaped response experiments and the mathematical model by finding optimal values for $\alpha$ and $\beta$. After the estimation of $\alpha$ and $\beta$ is completed, a figure comparing the experiments and the mathematical model is provided (Fig.~\ref{fig:calibration}). Write down the optimal values of $\alpha$ and $\beta$ below.
		
			\fbox{%
  				\parbox{0.92\textwidth}{
  				\vspace{0.2cm}
   				$\alpha$ =\\
   				$\beta$ =
   				\vspace{0.2cm}
  				}%
			}

		\item Calculate the equillibrium fan speed $\bar{u}$ using Eq.~\ref{eq:operating_point}. Use the following values for the constants: $\rho = 1.225~kg \cdot m^{\text{-}3}$, $m = 0.00283~kg$, $A = 4 \pi r^2$ with $r = 0.02~m$, $g = 9.81~m \cdot s^{\text{-}2}$, and $C_D = 0.47~(\text{-})$. Is the computed value sufficiently close to the observed value (Excercise~3.1.3)?

			\fbox{%
  				\parbox{0.92\textwidth}{
  				\vspace{0.2cm}
   				$\bar{u} = \left(\dfrac{2 m g}{\rho A C_D \alpha^2}\right)^{\dfrac{1}{2 \beta}} = $
   				\vspace{0.2cm}
  				}%
			}
	
	\item How is the goodness-of-fit of the mathematical model to the experimentally obtained data? What is the purpose of the validation experiment?
	
		\leegvakf{2cm}
		
\end{enumerate}
\end{opgave}

\mijnfiguur[h!]{width=\linewidth}{calibration.pdf}{Goodness-of-fit of the mathematical model (Eq.~\ref{eq:pingPongModelStates}) to the calibration and validation experiments (Fig.~\ref{fig:experiments}). The mean average error of the mathematical model in predicting the validation dataset is 2.2~cm.}{fig:calibration}

\pagebreak
\subsection{Tuning a PID controller}

In this section, you will learn how to tune a PID controller with the following transfer function,
\begin{equation}
C(s) = K_P + K_I~ \dfrac{1}{s} + K_D \underbrace{\left( \dfrac{s}{\left(1/K_F\right) s + 1} \right)}_{\text{filtered derivative}},
\end{equation}
where $K_P$ is the proportional gain, $K_I$ is the integral gain, $K_D$ is the derivative gain, and $1/K_F$ is the derivative filter first-order time constant. The PID controller can be implemented either directly in Simulink using the \texttt{PID} block, or using the following basic Simulink blocks,

\mijnfiguur[h!]{width=0.7\linewidth}{PID_simulink.pdf}{Implementation of a PID controller in Simulink. The derivation of the filtered derivative's transfer function is given in red.}{fig:PID_simulink}

\begin{opgave}[In-silico PID tuning]{}

	\begin{enumerate}
		\item Implement the mathematical model of the setup (Eq.~\ref{eq:pingPongModelStates}) with a PID controller in Simulink (Fig.~\ref{fig:PID_simulink}). Saturate the ball's height between 0~cm and 60~cm. Do this by implementing the equivalent of the following Matlab code in Simulink using two consecutive \texttt{Switch} blocks,
	\begin{lstlisting}[style=matlab]
	if z >= upper_bound
		zdot = min(0, v); % pass only negative velocities at upper bound
	elseif z <= lower_bound
		zdot = max(0, v); % pass only positive velocities at lower bound
	else
		zdot = v;
	end
	\end{lstlisting}
	
		Placing a \texttt{Saturation} block after the integration of Equations~\ref{eq:pingPongModelStates} in Simulink is incorrect and not equivalent to the above Matlab code. Do not model the in-flight dead time or noise on the sensor's output initially. Make sure the initial value of the integral control action is set to zero. Simulate a stepwise increase in the setpoint from 0~cm to 40~cm, and use the following controller gains $K_P=100$, $K_I=10$, $K_D=0$, $K_F=100$. Observe the output of the integral control action. What value does the integral control action converge to?
		
		\leegvakf{1cm}
		
		\item Simulate a step-wise increase in the setpoint height from 20~cm to 40~cm. Set the initial output of the integral control action to the equillibrium fan speed $\bar{u}$. Tune the PID controller, what values for $K_P$, $K_I$, $K_D$ and $K_F$ yield satisfactory behavior?
		
			\fbox{%
  				\parbox{0.92\textwidth}{
  				\vspace{0.2cm}
   				$K_P = $\\
   				$K_I = $\\
   				$K_D = $\\
   				$K_F = $
   				\vspace{0.2cm}
  				}%
			}
		
		\item Use a \texttt{Transport delay} block to model the in-flight dead time as a delay on the motor's output (be sure to set its initial output to the equillibrium fan speed $\bar{u}$). What is the impact of the dead-time on the stability of your previously tuned PID controller?
		
		\leegvakf{1cm}
		
		\item Use a \texttt{Spectral noise} (recommended) or \texttt{Random number} block to make the height measurement noisy. Subsequently filter the noisy signal using a low-pass filter (Excercise~3.3). Now, retune the PID controller. What values for $K_P$, $K_I$, $K_D$ and $K_F$ yield satisfactory behavior? 
		
			\fbox{%
  				\parbox{0.92\textwidth}{
  				\vspace{0.2cm}
   				$K_P = $\\
   				$K_I = $\\
   				$K_D = $
   				\vspace{0.2cm}
  				}%
			}		
		
		\item What is the impact of a noisy measurement on the derivative control action? What happens for high values of the proportional gain $K_P$ in the abscense of integral and derivative control action, and in the abscense of a setpoint change?
		
		\leegvakf{2cm}
		
		\item Simulate a stepwise decrease in the fan's effectiveness after a step response experiment, thereby increasing the fan's equillibrium speed $\bar{u}$. Model this by increasing the fan's proportionality constant $\alpha$ (Eq.~\ref{eq:pingPongModelStates}) by 5-10~\% using a \texttt{Step} block. Reassess the performance of your tuned controller.
		
		\leegvakf{2cm}
		
		\item (Optional) The Simulink model \textbf{ODEModelPID\_smithpredictor.slx} contains an implementation of the mathematical model of the setup (Eq.~\ref{eq:pingPongModelStates}), with a PID controller and with a Smith predictor to compensate for the dead time on the fan's motor response. Asses the stability of your previously tuned PID controller when a Smith predictor is used.
		
		\leegvakf{1cm}
		
	\end{enumerate}

\end{opgave}

\paragraph{Cohen-Coon tuning} The empirical tuning method by Cohen and Coon is an \textbf{open-loop tuning technique} relying on many complex non-linear system's step response being adequately approximated by a sigmoidal first-order transfer function with dead time (at least under/near the relevant operating conditions).
\begin{equation}
H(s) = \dfrac{y(s)}{u(s)} = \dfrac{K e^{-t_d s}}{\tau s + 1},
\end{equation}
where $K$ is the system's gain, $\tau$ its time constant, and $t_d$ its dead time. After applying a stepwise increase to the fan speed $u_{\text{step}}$ PWM units above the equillibrium fan speed $\bar{u}$, the gain $K$ can be computed as $K = \Delta y_{\text{step}}/u_{\text{step}}$, while the time constant $\tau$ and dead time $t_d$ can be estimated graphically. The former is the time needed to reach 63.2~\% of the step's output change $\Delta y_{\text{step}}$, while the latter is the elapsed time before a change in input has an effect on the system's output (Fig.~\ref{fig:cohen_coon_tuning}).\\

For our setup, it is best to use the in-flight dead time gathered in Excercise~3.4.2 instead of the lift-off dead time, as the latter is not representative of the system's behavior once the ball is airborne. Our choice to subtract the fan's equillibrium speed $\bar{u}$ from the step size is based on the intuition that this will better mimic a first-order response (remember the ball does not go anywhere for fan speeds under $\bar{u}$). Cohen and Coon devised that a stable closed-loop response can be obtained by computing the $K_P$, $K_I$ and $K_D$ values using the tuning rules listed in Table \ref{tab:cohen_coon}.

\mijnfiguur[h!]{width=\linewidth}{cohen_coon_tuning.pdf}{Using the block response experiments to estimate the gain, time constant and dead time of the approximate first-order response.}{fig:cohen_coon_tuning}

\begin{opgave}[Cohen-Coon tuning]{}
\end{opgave}
	\begin{enumerate}
		\item Use the block response experiments gathered during Excercise~3.4.1 to graphically estimate the gain $K$ and time constant $\tau$, both for the initial step (labeled 1 in Fig.~\ref{fig:cohen_coon_tuning}), as well as the upwards step during the U-shaped phase of the experiment (labeled 2 in Fig.~\ref{fig:cohen_coon_tuning}). Tune the PID controller using the tuning rules of Cohen-Coon listed in Table~\ref{tab:cohen_coon}.
		
		\leegvakf{2cm}
		
		\item Simulate the step response of the closed-loop system using the tuned P, PI and PID controllers. What controllers lead to a stable closed-loop response?
		
		\leegvakf{2cm} 
		
	\end{enumerate}

\begin{table}[h!]
\caption{Tuning rules of Cohen-Coon for a PID controller $C(s) = K_P + K_I/s + K_D s$.}
\centering
 \begin{tabular}{|c | c c c|} 
 \hline
  & $K_P$ & $K_I$ & $K_D$ \\  
 \hline
 P & $\dfrac{1}{K} \dfrac{\tau}{t_d} \left( 1 + \dfrac{t_d}{3 \tau} \right) $ & - & - \\ [3mm] 
 PI & $\dfrac{1}{K} \dfrac{\tau}{t_d} \left( 0.9 + \dfrac{t_d}{12 \tau} \right) $ & $K_P*\left(\dfrac{1}{t_d}~\dfrac{9 + 20 (t_d/\tau)}{30 + 3 (t_d/\tau)} \right)$ & - \\ [3mm] 
 PID & $\dfrac{1}{K} \dfrac{\tau}{t_d} \left( 4/3 + \dfrac{t_d}{4 \tau} \right) $ & $K_P*\left(\dfrac{1}{t_d}~\dfrac{13 + 8 (t_d/\tau)}{32 + 6 (t_d/\tau)} \right)$ & $K_P*\left( t_d~\dfrac{4}{11 + 2 (t_d/\tau)}\right)$ \\ [3mm] 
 \hline
 \end{tabular}
 \label{tab:cohen_coon}
\end{table}

\paragraph{Ziegler-Nichols tuning} Opposed to the method of Cohen and Coon, the empirical tuning method of Ziegler and Nichols is a \textbf{closed-loop tuning technique}. First, the system is stabilised in a desired operating point. Then, the controller is reduced to its P-action, and a change in the setpoint is demanded. The proporational controller gain $K_P$ is then increased until the system's closed loop response to the demanded setpoint change results in permanent oscillations. This gain, often referred to as the \textit{ultimate gain} $K_u$, as well as the period of the continuous oscillations $P_u$ are recorded and used to tune the system (Table~\ref{tab:ziegler_nichols_tuned}).

\begin{opgave}[Empirical PID tuning methods: Ziegler-Nichols]{}
	\begin{enumerate}
		\item Determine the ultimate control gain $K_u$ and the period of the associated oscillations $P_u$ using your simulink model of the setup (Excercise~3.7). Tune the controller using the tuning rules in Table~\ref{tab:ziegler_nichols}.
		
		\leegvakf{3cm}
		
		\item Simulate a step-wise change in the setpoint from 20~cm to 40~cm, do the controllers yield a satisfactory response?
		
		\leegvakf{2cm}
		
	\end{enumerate}
\end{opgave}

\begin{table}[h!]
\caption{Tuning rules of Ziegler-Nichols for a PID controller $C(s) = K_P + K_I/s + K_D s$.}
\centering
 \begin{tabular}{|c | c c c|} 
 \hline
  & $K_P$ & $K_I$ & $K_D$ \\
 \hline
 P & $\dfrac{K_u}{2}$ & - & - \\ [3mm] 
 PI & $\dfrac{K_u}{2.2}$ & $\dfrac{1.2 K_P}{P_u}$ & - \\ [3mm] 
 PID & $\dfrac{K_u}{1.7}$ & $\dfrac{2 K_P}{P_u} $ & $\dfrac{8 K_P}{P_u} $ \\ [3mm] 
 \hline
 \end{tabular}
 \label{tab:ziegler_nichols}
\end{table}

\subsection*{Part III: PID control of the experimental set-up}

In this part of the practical, you will test your tuned PID controllers on the experimental setup and assess their performance. You will examine the frequency response of the closed-loop system and construct its Bode diagram, which you will then compare to the open-loop Bode diagram (Excercise~3.5). By using PID controllers in practice you will gain a deeper understanding of some common issues such as noisy measurements and dead time. 

\subsection{Testing PID control on the experimental setup}

\begin{opgave}[PID control of the experimental set-up]{}
	\begin{enumerate}
		\item  Open the Simulink model \textbf{PID.slx}, which contains the implementation of a PID-controller. Set adequate parameters for the low pass filtering of the IR sensor's measurement (Excercise~3.3). Verify the initial condition of the integral controller's \texttt{Integrate} block is set to the fan's equillibrium speed $\bar{u}$ (Excercise~3.6.2). The height setpoint, controller gains ($K_P$, $K_I$, $K_D$, $K_F$) and the time constant of the height measurement's low pass filter $\tau_F$ can be tuned using the knobs while operating the experimental setup. Use the knobs to configure your optimal PID-controller. Change the setpoint from 0~cm to 40~cm and observe the response. Disturb the system by constricting the airflow with your hands. Does your controller work adequately?

		\leegvakf{2cm}
		
	\end{enumerate}	
\end{opgave}

\begin{opgave}[Contribution of the different control actions]{}
	\begin{enumerate}
		\item Set the initial condition of the integral controller's \texttt{Integrate} block to zero for the duration of this excercise. Use the \textit{Scope} to visualise the \textbf{individual contributions of the proportional, integral and derivative actions} of the controller. Start with the ball at the bottom of the tube. Set the proporational gain to $K_P = 600-800$, while disabling the integral and derivative control ($K_I=K_D=0$). Raise the setpoint to 40~cm. Does the ball ever reach the setpoint? How is this phenomenon called?

			\leegvakf{1cm}

		\item Start with the ball at the bottom of the tube. Disable the proportional and derivative control by setting $K_P = K_D = 0$. Set the integral gain to $K_I = 50$. Raise the setpoint to 40~cm. What happens to the contribution of the I-action? Is the obtained system stable?
		
			\leegvakf{1cm}

		\item Starting with the ball stabilised at 40~cm, disable the integral and derivative control action by setting $K_I = K_D = 0$. Make stepwise changes in the setpoint and disturb the system. Is the system stable and its response satisfactory? Do you feel like any derivative action is needed at this point? 

			\leegvakf{1cm}
			
		\item Starting with the ball stabilised at 40~cm, disable the integral and derivative control action by setting $K_I = K_D = 0$. Make the fan slightly less effective by holding your hand flat above the tube at some distance (circa 5~cm). Is the controller able to keep the ball at 40~cm? Restabilise the system at 40~cm and make the fan slightly less effective, but set the integral gain to $K_I=10$. What happens to the output of the integral controller? Reduce the fan's efficacy at least 30~s and then remove your hand. What phenomenon do you observe?
		
		\leegvakf{1cm}
			
	\end{enumerate}
\end{opgave}

\begin{opgave}[Effect of filtering on the derivative action]{}
	\begin{enumerate}
		\item Start with the ball stabilised at 40~cm, set the derivative filter's gain to $K_F = 1$ and increase the derivative gain to $K_D = 200\text{-}300$. Take some stepwise changes in the setpoint. What do you observe?
		
			\leegvakf{2cm}
			
		\item Examine the effect of changing the derivative filter's gain $K_F$, the time constant of the first order derivative filter is equal to $\tau = 1/K_F$.
		
			\leegvakf{2cm}
	\end{enumerate}
\end{opgave}

\begin{opgave}[Effect of dead time on stability]{}
	\begin{enumerate}
		\item In \textbf{PID.slx}, add a \texttt{Transport delay} block of 1~s to the measurement of the ball's height to introduce additional dead time. Use stable controller gains and raise the setpoint from 0~cm to 40~cm. What is the effect of the added dead time on the stability of the controlled system?
	
		\leegvakf{1 cm}
	
	\end{enumerate}
\end{opgave}

\subsection{Understanding the system's closed-loop frequency response}

Finally, in analogy to Excercise~3.5, you will investigate the system's closed-loop frequency response. You will do this by applying a sinusoidal change of the height setpoint and observing the amplitude of the resulting sinusoidal changes in the ball's height, as well as the phase shift between the input and output signals. Using your observations, you will construct an approximate \textbf{Bode diagram}. 

\begin{opgave}[Frequency response of the system]{}
	\begin{enumerate}
		\item  Open the Simulink model \textbf{frequencyPID.slx} and use the knobs to set your optimal controller gains. Make sure the initial condition of the integral controller's \texttt{Integrate} block is set to the fan's equillibrium speed $\bar{u}$. The setpoint varies sinusoidally around 35~cm with an amplitude of 10~cm and a variable frequency. The frequency can be changed using the knob, start a high frequency of 10~rad/s. What is the amplitude of the sinusoidal changes in the ball's height? Are the input and output signals in or out of phase?
		
		\leegvakf{1cm}
		
		\item Decrease the frequency of the input signal to 3~rad/s. How does the amplitude of the ball's height change? Are the input and output signals in or out of phase?
		
		\leegvakf{1cm}
		
		\item Decrease the frequency of the input signal to around 2~rad/s. What is the amplitude of the ball's height? Are the input and output signals in or out of phase?
		
		\leegvakf{1cm}
		
		\item Decrease the frequency of the input signal to around 1~rad/s. What is the amplitude of the ball's height? Are the input and output signals in or out of phase?
		
		\leegvakf{1cm}
		
		\item Decrease the frequency of the input signal to around 0.5~rad/s. What is the amplitude of the ball's height? Are the input and output signals in or out of phase?
		
		\leegvakf{1cm}
		
		\item Draw an approximate Bode diagram of the system. What kind of system is the Bode diagram characteristic of?
	\end{enumerate}
\end{opgave}

		\begin{figure}[h!]
			\centering
			
			
			\caption{Approximate Bode diagram based on the setup's closed-loop frequency response.}
 		\end{figure}

\subsection*{Part IV: Advanced control strategies}

\subsection{Linear-Quadratic Regulator with Luenberger state observer}

\subsubsection{Control strategy and design}
\paragraph{Linear-Quadratic Regulator} In this section, we design an optimal state feedback controller to control the height of our table tennis ball. Mathematically, we attempt to drive our non-linear system to a desired operating point $\bm{x_{\text{sp}}} = (z, v)$ using an input $u(t)$. To accomplish this, the input $u(t)$ is chosen as the sum of two components (Fig.~\ref{fig:nonLinearControl_withTTS}): The first, $\bar{u}$, is the input needed to keep the system in an operating point, and is the solution to the equation $\bm{\dot{x}(t)} = \bm{f}(\bm{x(t)}, \bar{u}) = 0$ (Eq.~\ref{eq:operating_point}). The second, $u^*$, is the force needed to drive the system from any initial condition to the desired operating point, mathematically, $u^* = \bm{K} (\bm{x} - \bm{x_{\text{sp}}})$, which is the product of the feedback gain matrix $\bm{K}$ and the deviation from the setpoint.\\

The values of the feedback matrix K must then be chosen so that the real parts of the eigenvalues of the (linearised) system with state feedback $(\bm{A} + \bm{B} \cdot \bm{K})$ are negative, stabilizing the operating point. This is possible if the system is controllable, which we have previously verified (Eq.~\ref{eq:controllability}). For nonlinear systems the feedback matrix $\bm{K}$ is typically designed using the system matrix $\bm{A}$ and input matrix $\bm{B}$ from the system linearised in the operating point (Eq.~\ref{eq:linearised_system}). However, this strategy should always be used with care as nonlinear systems may have multiple operating points\footnote{Linear systems have only one operating point!}and the size of the stable region around the desired operating point is unknown. Our system has an infinite number of operating points, as the ball can be stabilised at any height $z$ inside the tube as long as the fan's hover speed $\bar{u}$ is maintained. However, because each operating point is neutrally stable, designing the gain matrices based on a linearised system is likely to work.\\

Instead of intuitively choosing the entries of the gain matrix $\bm{K}$ to obtain negative eigenvalues for the system with state feedback, it is possible to design an \textit{optimal} gain matrix $\bm{K}$. Doing so entails defining the desired qualities of an \textit{optimal} controller and translating them into an objective function. Typically, these qualities are: 1) Reaching the setpoint quickly, where a state-cost matrix $\bm{Q}$ governs the relative importance of reaching the setpoint of different states. For our setup, asigning more importance to reaching the height setpoint than the velocity setpoint ($v=0~m \cdot s^{\text{-}1}$) will result in oscillations. 2) Minimise the cost needed to reach the setpoint, where an input-cost matrix $\bm{R}$ governs the relative importance (read price) of using different inputs to reach the setpoint. Because our system has only one input, the input-cost matrix is not relevant to this practical. 3) To avoid offset. Minimising this objective function yields an optimal gain matrix $\bm{K}$, which is referred to as the Linear-Quadratic Regulator.\\

\begin{opgave}[Designing an appropriate state feedback gain matrix $\bm{K}$]{}
	\begin{enumerate}
		\item What size should the state feedback gain matrix $\bm{K}$ be?
		
		\leegvakf{1cm}
		
		\item Use the system matrix $\bm{A}$ and input matrix $\bm{B}$ of the linearised system (Eq.~\ref{eq:linearised_system}) to design a suitable state feedback gain matrix $\bm{K}$. Do this symbolically in Wolfram Mathematica by evaluating Eq.~\ref{eq:linearised_system} in an operating point $\bm{x^*} = \left(z^*,~ 0,~ \bar{u}\right)$, and then computing conditions for the entries of $\bm{K}$ to make the eigenvalues of $\bm{A} + \bm{B K}$ negative.
		
		\leegvakf{2cm}
		 
		 \item Implement the mathematical model of the setup (Eq.~\ref{eq:pingPongModelStates}; Excercise 3.7.1) with state feedback (Fig.~\ref{fig:nonLinearControl_withTTS}) in Simulink. Implement dead time on the fan's motor response (Excercise~3.4.2). Assume the position and velocity of the ball are both known so no Luenberger state observer is needed. Simulate a step in the setpoint from 20~cm to 40~cm. Assess the response for different state feedback gain matrices. Use the builtin Matlab function \texttt{lqr(A, B, Q, R)} to design state feedback gain matrices. Experiment with varying the state-costs of the height setpoint $Q_{11}$ and the velocity setpoint $Q_{22}$ when designing LQR gains. Find a suitable gain matrix to try out on the experimental setup.
		 
		 \leegvakf{1cm}
		 
	\end{enumerate}
\end{opgave}
		
\paragraph{Luenberger state observer} Only the position of the table tennis ball is monitered by the IR sensor while state feedback requires all system states, both the position and velocity of the table tennis ball, to be known. To resolve this problem, a Luenberger state observer can be designed because the system is observable (Eq.~\ref{eq:observability}). Similar to the state feedback, the observer is designed using the linearised system. The state observer is a linear system consisting of a predictor and a corrector,
\begin{equation}
\underbrace{\bm{\dot{\hat{x}}} = \bm{A\hat{x}} + \bm{B u}}_{\text{predictor}} + \underbrace{ \bm{L} \left(\bm{y} - \bm{C \hat{x}} - \bm{D u} \right)}_{\text{corrector}} 
\end{equation}
which models the evolution of the system's states $\bm{\hat{x}} = (\hat{z},~ \hat{v})$ by using the sensor's measurement of the ball's height $y$, the fan speed $u$, and a (linearised) process model as its inputs. The predictor, $\bm{\dot{\hat{x}}} = \bm{A \hat{x}} + \bm{B u}$, uses the system's (linearised) process model, inputs $u(t)$ and an initial condition to compute the dynamic trajectory of the system's states. However, the predicted state trajectory will diverge from the actual state trajectory as time progresses. Therefore a corrector term, $\bm{ L \left(y - C \hat{x} - D u} \right)$, equal to $\bm{L}$ times the difference between the sensor's measurement $y$ and the predicted measurement using the model $\hat{y} = C \hat{x} - D u$, is added to the equation. Designing the matrix $\bm{L}$ so that the eigenvalues of the matrix $(\bm{A} - \bm{L C})$ are strongly negative drives the predictive error of the observer $\bm{\epsilon} = \bm{x -\hat{x}}$ to zero. For a controllable and observable system, the \textbf{separation principle} states that matrices $\bm{K}$ and $\bm{L}$ can be designed independently.

\begin{figure}[h]
	\centering
	\begin{tikzpicture}[auto, node distance=2.5cm,>=latex']
	
	\node [block] (system) {
		$\begin{aligned}
		\dot{\bm{x}}&=\bm{f}(\bm{x},\bm{u})\\
		\bm{y}&=\bm{x}
		\end{aligned}$
		};
		
	\node [block, below = 1.0cm of system] (ttk) {
	$K(\bm{\hat{x}} - \bm{x_{sp}})$
	};
	
	\node [block, right = 1.0cm of system] (tts) {
	$\dot{\bm{\hat{x}}} = \bm{A \hat{x}} + \bm{B u} + \bm{L} (\bm{y} - \bm{C \hat{x}} - \bm{D u})$
	};
	
	\node [output, right = 1.5 cm of tts] (output) {};
	
	\node [above = 0.5cm of tts] (u) {$\bm{u}$};
	\draw [->] (u) -- node [] {}(tts);
	
	\draw [->] (tts) -- node [name=tts_output] {$\bm{\hat{x}}$}(output);
	
	\draw [->] (system) -- node [name=system_tts] {$\bm{y}$}(tts);
	
	\node [circle, draw, black, minimum size=5mm, inner sep=0pt,below = 0.5 cm of tts_output] (sum1) {$-$};
	
	\node [right = 0.5cm of sum1] (xbar) {$\bm{x}_{sp}$};
	
	\draw [->] (xbar) -- node [] {}(sum1);
	\draw [->] (tts_output) -- node [] {}(sum1);
	\draw [->] (sum1) |- node [] {}(ttk);
	
	\node [circle, draw, black, minimum size=5mm, inner sep=0pt,left = 1 cm of system] (sum2) {$+$};
	
	\draw [->] (ttk) -| node [near end] {$\bm{u}^\ast$}(sum2);
	\draw [->] (sum2) -- node [] {$\bm{u}$}(system);
	
	\node [block, left = 1.0 cm of sum2] (solve) {
	$\begin{aligned}
	& \text{Solve} \\
		& \bm{\dot{x}(t)} = \bm{f}(\bm{x(t)}, \bar{u}) = 0
		\end{aligned}$};
	%\draw [->,preaction={draw,white,line width=5pt}] (xbar) |- node {} (solve);
	\draw [->] (solve) -- node [near end] {$\bar{\bm{u}}$} (sum2);
	\end{tikzpicture}
	\caption{Schematic representation of a state feedback strategy with Luenberger state observer to bring a non-linear system to a setpoint $\bm{x_{\text{sp}}}$.}
	\label{fig:nonLinearControl_withTTS}
\end{figure}

\begin{opgave}[Designing an appropriate corrector gain matrix $\bm{L}$]{}
	\begin{enumerate}
		\item What size should the corrector gain matrix $\bm{L}$ be?
		
		\leegvakf{1cm}
		
		\item Use the system matrix $\bm{A}$ and output matrix $\bm{C}$ of the linearised system (Eq.~\ref{eq:linearised_system}) to design a suitable state observer corrector gain matrix $\bm{L}$. Do this symbolically in Wolfram Mathematica by evaluating Eq.~\ref{eq:linearised_system} in an operating point $\bm{x^*} = \left(z^*,~ 0,~ \bar{u}\right)$, and then computing conditions for the entries of $\bm{L}$ to make the eigenvalues of $\bm{A} - \bm{L C}$ negative.
		
		\leegvakf{3cm}
		
		\item Adjust your Simulink implementation of the mathematical model of the setup with state feedback (Excercise~3.15.4) to include a Luenberger state observer. Based on the separation principle, the state feedback gain matrix $\bm{K}$ and the corector gain matrix $\bm{L}$ can be designed independently. Assume only the position of the ball is measured and add artifical measurement noise, which you subsequently filter (Excercise~3.7.4). Simulate a step in the setpoint from 20~cm to 40~cm and visualise the difference between the measured and estimated heights of the table tennis ball, as well as the estimated velocity, for different corrector gain matrices $\bm{L}$.
		
		 \leegvakf{1cm}
		
	\end{enumerate}
\end{opgave}

%\begin{figure}[h]
%	\centering
%	\begin{tikzpicture}[auto, node distance=2.5cm,>=latex']
%	
%	\node [block] (system) {
%		$\begin{aligned}
%		\dot{\bm{x}}&=\bm{f}(\bm{x},\bm{u})\\
%		\bm{y}&=\bm{x}
%		\end{aligned}$
%		};
%		
%	\node [block, below = 1.0cm of system] (ttk) {
%	$K(\bm{x} - \bm{x_{sp}})$
%	};
%	
%	\node [output, right = 3.5 cm of system] (output) {};
%	
%	\draw [->] (system) -- node [name=y] {$\bm{x}$}(output);
%	
%	\node [circle, draw, black, minimum size=5mm, inner sep=0pt,below = 0.5 cm of y] (sum1) {$-$};
%	
%	\node [right = 0.5cm of sum1] (xbar) {$\bm{x}_{sp}$};
%	
%	\draw [->] (xbar) -- node [] {}(sum1);
%	\draw [->] (y) -- node [] {}(sum1);
%	\draw [->] (sum1) |- node [] {}(ttk);
%	
%	\node [circle, draw, black, minimum size=5mm, inner sep=0pt,left = 1 cm of system] (sum2) {$+$};
%	
%	\draw [->] (ttk) -| node [near end] {$\bm{u}^\ast$}(sum2);
%	\draw [->] (sum2) -- node [] {$\bm{u}$}(system);
%	
%	\node [block, left = 1.0 cm of sum2] (solve) {
%	$\begin{aligned}
%	& \text{Solve} \\
%		& \bm{\dot{x}(t)} = \bm{f}(\bm{x(t)}, \bar{u}) = 0
%		\end{aligned}$};
%	%\draw [->,preaction={draw,white,line width=5pt}] (xbar) |- node {} (solve);
%	\draw [->] (solve) -- node [near end] {$\bar{\bm{u}}$} (sum2);
%	\end{tikzpicture}
%	\caption{Schematic representation of a state feedback strategy to bring a non-linear system to a setpoint $\bm{x_{\text{sp}}}$.}
%	\label{fig:nonLinearControl}
%\end{figure}

\subsubsection{Testing LQR control on the experimental setup}

\begin{opgave}[LQR control of the experimental setup]{}
	\begin{enumerate}
		\item Open the Simulink model \textbf{LQR.slx}, which contains the implementation of an LQR controller. Be sure to change the solution algorithm to the fixed-step Backward Euler \texttt{ode1be} method. The state feedback gain matrix's elements $k_{11}$ and $k_{12}$ can be tuned using the knobs. Raise the setpoint from 0~cm to 40~cm and observe the system's response. How does the response compare to that of a PID controller?
		
		\leegvakf{1cm}
		
	\end{enumerate}
\end{opgave}

%\begin{opgave}[Frequency response of the LQR controller]{}
%	\begin{enumerate}
%		\item Open the Simulink model \textbf{frequencyLQR.slx}, which uses an LQR controller to vary the height setpoint sinusoidally around 35~cm with an amplitude of 10~cm and a variable frequency. Similar to Excercise~3.14 the frequency can be changed using the knob, start at a high frequency of 10~rad/s, and lower the setpoint frequency stepwise to 0.5~rad/s. Record the relative amplitude and phase shift of the sinusoidal changes in the ball's height and use them to draw an approximate Bode diagram below. Is the response more or less stable than with a PID controller? How can you deduce this from the Bode diagram?
%		
%		\leegvakf{1cm}
%		
%	\end{enumerate}
%\end{opgave}
%	
%\begin{figure}[h!]
%	\centering
%	\includegraphics[width=0.72\linewidth]{bode_diagram_empty_1.pdf}
%	\includegraphics[width=0.72\linewidth]{bode_diagram_empty_2.pdf}
%	\caption{Approximate Bode diagram based on the setup's closed-loop frequency response with an LQR controller.}
% 		\end{figure}

\section{Solutions}

\subsection*{Linearisation, controllability and observability in Wolfram Mathematica}

The following Wolfram Mathematica code was used to compute the derivatives of Eq.~\ref{eq:pingPongModelStates} symbolically, in order to obtain a linearised mathematical model of the setup (Eq.\ref{eq:linearised_system}, Section~\ref{section:stability}). Mathematica was further used to check the controllability and observability of the setup (Section~\ref{section:controllability}). 

\begin{lstlisting}[style=mathematica]
(*Linearise system symbolically*)
Clear[v, u, rho, r, A, Cd, m, g, alpha, beta]
f = {{v}, {(0.5*rho*A*Cd/m)*(alpha*u^beta - v)^2 - g}} ;
FullSimplify[D[f, z]]
FullSimplify[D[f, v]]
FullSimplify[D[f, u]]

(*Define linearized model in generic point x=(z,v,u)*)
a = {{0, 1}, {0, (rho*A*Cd/m)*(v - alpha*u^beta)}};
b = {{0}, {(alpha*beta*rho*A*Cd/m)*u^(beta - 1)*(alpha*u^beta - v)}};
c = {{1, 0}};
d = {{0}};
model = StateSpaceModel[{a, b, c, d}]

(*Check controllability*)
v = 0;
FullSimplify[ControllabilityMatrix[model]]
MatrixRank[ControllabilityMatrix[model]]
ControllableModelQ[model]

(*Check observability*)
ObservabilityMatrix[model]
MatrixRank[ObservabilityMatrix[model]]
ObservableModelQ[model]
\end{lstlisting}

\subsection*{Excercise 3.1}

\begin{enumerate}
\setlength\itemsep{0em}
	\item NA.
	\item Approximately 162 (may differ from setup to setup).
	\item Approximately 152 (may differ from setup to setup).
	\item Approximately 153 (may differ from setup to setup). Because the fan speed needed to hover the ball at 30~cm and 50~cm are almost identical, the assumption that there is no pressure drop along the length of the tube is valid. In other words, the air's speed in the tube is quasi-independent of the position in the tube and hence Eq.~\ref{eq:assumption_no_pressure_drop} is valid.
\end{enumerate}

\subsection*{Excercise 3.2}

\begin{enumerate}
\setlength\itemsep{0em}
\item NA.
\item The signal is noisy and its overall quality is poor, especially when the table tennis ball is in the bottom 20~cm of the tube. This is caused by the low sensitivity of the sensor in this region (Fig.~\ref{fig:sensor_calibration}). Between 58~cm - 63~cm, the sensor falsly thinks the ball's height drops to around 40~cm.
\end{enumerate}

\subsection*{Excercise 3.3}

\begin{enumerate}
\setlength\itemsep{0em}
\item An example of a Simulink model can be found in Fig.~\ref{fig:readProximity_sol}. The signal quality has improved.
\item The low pass filter introduces a delay in the signal (dead time). A lower time constant results in a noisier signal but less dead time. A higher time constant results in a smoother but more delayed signal. Finding an appropriate time constant is a balancing act between signal quality and dead time. Both a poor quality signal quality and dead time lower a feedback controller's ability to stabilise the system. We recommend a (fast) filter time constant $\tau_F = 0.05\text{-}0.10~s$ when using a PID controller on the experimental setup.
\item A low-pass filter, which amplifies low-frequency signals and attenuates high-frequency signals. In our case, the sensor's noise is in the high-frequency spectrum. 
\end{enumerate}

\subsection*{Excercise 3.4}

\begin{enumerate}
\setlength\itemsep{0em}
	\item See Fig.~\ref{fig:blockResponse}.
	\item $t_d \approx 0.5~s$, see Fig.~\ref{fig:wResponse}.
\end{enumerate}

\subsection*{Excercise 3.5}

\begin{enumerate}
\setlength\itemsep{0em}
\item The amplitude of the sinusoidal changes in the ball's height (output signal) is very small, almost non-existent. The ball hovers in the tube.
\item As the frequency of the input signal is lowered, the amplitude of the output increases. The input and output signals are almost fully out of phase (-180~degrees).
\item The amplitude of the output now covers the entire length of the tube. The ball starts at the bottom of the tube and reaches the top of the tube during each cycle. Ignoring the dead time induced by the additional energy needed to get the ball in the air, the input and output signals are now more or less in phase (0~degrees).
\item The approximate Bode diagram is characteristic of a first-order system (Fig.~\ref{fig:approx_bode_diagram_open}). The system's breakout frequency is located at approximately 1~rad/s. As previously discussed, a first-order system is a low-pass filter, as low-frequency inputs are amplified while high-frequency inputs are attenuated. 
\end{enumerate}

\subsection*{Excercise 3.6}

\begin{enumerate}
\setlength\itemsep{0em}
\item $\alpha=0.19,~\beta=0.63$. May differ between setups.
\item $\bar{u} = 151$, and thus in line with the value found during Excercise~3.1.
\item The mathematical model is able to adequately describe the time course of the validation experiment (Fig.~\ref{fig:calibration}), as gauged by a small mean average error of 2.2~cm. Performing \textit{out-of-sample} testing on a \textit{validation} dataset allows us to confidently assert the validity and predictive performance of our mathematical model. Other performance indicators could be the values of the parameters, which must make sense if the parameters have physical meaning, or the size of confidence intervals on the parameter estimates (obtained using the Fisher Information Matrix or Markov-Chain Monte-Carlo sampling).
\end{enumerate}

\subsection*{Excercise 3.7}

\begin{enumerate}
\setlength\itemsep{0em}
\item The integral control action converges to $\bar{u}$ (Fig.~\ref{fig:tuned_PID1}). The PID controller's integral action thus `learns' what fan speed is needed to hover the ball. Therefore, it is best to initialise the integral control action as $\bar{u}$ (\texttt{Initial condition} in the I-controller's \texttt{Integrate} block). The Simulink model, including the in-flight dead time and noisy measurements, is shown in Figs.~\ref{fig:ODEModelPID}, \ref{fig:ODEModelPID_system}, and \ref{fig:ODEModelPID_zdot}.
\item $K_P=1000;~ K_I=0;~ K_D=100;~K_F=1$ (Fig.~\ref{fig:tuned_PID2}). 
\item More in-flight dead time destabilises the closed-loop response (Fig.~\ref{fig:tuned_PID3}).
\item $K_P=50;~ K_I=0;~K_D=0;~K_F=1$ (Fig.~\ref{fig:tuned_PID4}).
\item The derivative control action destabilises the closed-loop response. Large proportional gains can also destabilise the closed-loop system, even in the abscence of a setpoint change, this is due to the combination of the sensor's noise and the system's dead time (Fig.~\ref{fig:tuned_PID5}).
\item As the I-controller is essentially `learning' how to hover the ball by finding $\bar{u}$, setting $K_I = 0$ makes the system incapable of adjusting $\bar{u}$. However, external disturbances, such as the electronic components ``warming up'', may cause changes of $\bar{u}$ over time. Therefore, the use of only a P-controller will make the system incapable of handling external disturbances (Fig.~\ref{fig:tuned_PID6}). An alternative controller's response ($K_P=80;~ K_I=10;~ K_D=50;~K_F=1$) is shown in Fig.~\ref{fig:tuned_PID7}.
\item The use of a Smith predictor enhances the closed-loop stability of the system. Higher proportional gains $K_P$ can now be applied before the system becomes unstable. 
\end{enumerate}

\subsection*{Excercise 3.8}

\begin{enumerate}
\setlength\itemsep{0em}
\item The controller gains tuned using the empirical method by Cohen and Coon are shown in Tables \ref{tab:cohen_coon_tuned1} and \ref{tab:cohen_coon_tuned2}.
\item The response to a step-wise increase in the setpoint height from 20~cm to 40~cm for the controllers listed in Table~\ref{tab:cohen_coon_tuned1} are shown in Fig.~\ref{fig:tuned_PID_cohencoon} (with dead time but without noisy measurements). Only the P-controller leads to an adequate closed-loop response, the tuned integral gains $K_I$ are too high to achieve a stable closed-loop response. Note how there is no offset when using a P-controller (Q: How is this related to the system's stability?). The Cohen-Coon tuning rules are based on the assumption that the system's response are adequately approximated by a linear first-order system. As our system is non-linear with neutral stability, the approximation likely does not hold. Always use empirical tuning rules based on linear approximations with care when designing a suitable controller.
\end{enumerate}

\begin{table}[h!]
\caption{Controller gains tuned using the empirical method by Cohen and Coon. For an initial step size of $u_{\text{max}} = 170$, $K = 0.5 / (170 - 151) = 0.026$, $\tau = 0.8~s$ and $t_d = 0.5~s$.}
\centering
 \begin{tabular}{|c | c c c|} 
 \hline
  & $K_P$ & $K_I$ & $K_D$ \\ [0.5ex] 
 \hline
 P & 73 & - & - \\ [3mm] 
 PI & 58 & 78 & - \\ [3mm] 
 PID & 91 & 91 & 14 \\ [3mm] 
 \hline
 \end{tabular}
 \label{tab:cohen_coon_tuned1}
\end{table}

\begin{table}[h!]
\caption{Controller gains tuned using the empirical method by Cohen and Coon. For an upwards step during the U-shaped response part of the block response experiments with $u_{\text{step}} = 10$, $K = (0.5 - 0.1) / 10 = 0.0025$, $\tau = 1.5~s$ and $t_d = 0.5~s$.}
\centering
 \begin{tabular}{|c | c c c|} 
 \hline
  & $K_P$ & $K_I$ & $K_D$ \\ [0.5ex] 
 \hline
 P & 67 & - & - \\ [3mm] 
 PI & 56 & 56 & - \\ [3mm] 
 PID & 85 & 92 & 15 \\ [3mm] 
 \hline
 \end{tabular}
 \label{tab:cohen_coon_tuned2}
\end{table}

\subsection*{Excercise 3.9}

\begin{enumerate}
\setlength\itemsep{0em}
\item The ultimate control gain $K_u \approx 114$ and the period of the resulting permanent oscillation $P_u \approx 3.5~s$ were determined in silico using the calibrated mathematical model (Fig.~\ref{fig:tuned_PID_zieglernichols_1}). It is possible to determine the ultimate control gain using the setup. The gains of the controllers tuned using the rules of Ziegler and Nichols are given in Table~\ref{tab:ziegler_nichols_tuned}.

\item The resulting system's closed-loop response using the tuned controller gains is shown in Fig.~\ref{fig:tuned_PID_zieglernichols_2}. The P and PI controllers provide a stable closed-loop response while the PID controller does not. The P controller's response is preferred over the PI controller's response. Similar to the tuning method of Cohen and Coon, the integral gain $K_I$ is too high. Based on the empirical method from Ziegler-Nichols, the use of a P-controller seems most adequate. 
\end{enumerate}

\begin{table}[h!]
\caption{Controller gains tuned using the empirical method by Ziegler and Nichols. For an ultimate control gain $K_u \approx 114$ and period of the resulting permanent oscillation of $P_u \approx 3.5~s$.}
\centering
 \begin{tabular}{|c | c c c|} 
 \hline
  & $K_P$ & $K_I$ & $K_D$ \\ [0.5ex] 
 \hline
 P & 57 & - & - \\ [3mm] 
 PI & 52 & 17.8 & - \\ [3mm] 
 PID & 67 & 38.3 & 153 \\ [3mm] 
 \hline
 \end{tabular}
 \label{tab:ziegler_nichols_tuned}
\end{table}

\subsection*{Excercise 3.10}

\begin{enumerate}
	\setlength\itemsep{0em}
	\item The controller with gains $K_P=80;~ K_I=10;~ K_D=50;~ K_F=1$, and filter time constant $\tau_F=0.05~s$ works adequately for setpoint changes and disturbances (Excercise 3.7.6). Note how the integral controller's output converges to $\bar{u}$ (at least after some time, as the electronic components warm up).
\end{enumerate}

\subsection*{Excercise 3.11}

\begin{enumerate}
	\setlength\itemsep{0em}
	\item No, the ball will repeatedly go up and down the tube. The ball's average position will be located below the setpoint, and this is termed ``offset''.
	\item The I ccontroller's output gradually increases to a value over the fan's equillibrium speed $\bar{u}$, raising the ball of the stand. As the ball crosses the desired setpoint, the I controller's starts gradually decreasing but too slow; the ball makes it way to the top of the tube. As the I controller's output gradually decreases back under the fan's equillibrium speed $\bar{u}$, the ball starts making its way down the tube again and the cycle is repeated. The obtained system is oscillatory and thus unstable, the I controller suffers from ``windup''.
	\item With the proportional gain set to $K_P = 80$, the system's reaction to setpoint changes and disturbances is adequate and stable. Integral or derivative action does not seem needed.
	\item Without the integral controller `learning' the new (increased) equillibrium fan speed $\bar{u}$, the controller is unable to maintain a height of 40~cm. With the integral controller enabled, its output gradually increases and the ball maintains its height of 40~cm. Removing the disturbance suddenly results in ``integral windup''. 
\end{enumerate}

\subsection*{Excercise 3.12}
\begin{enumerate}
	\setlength\itemsep{0em}
	\item The system becomes less stable because the derivative controller amplifies the high-frequent noise from the sensor. Intuitively, this makes sense: measurement noise is a small change in the absolute value of the measurement over a very small period of time. Noise thus has a large rate of change (derivative), resulting in a large D-controller action. What you observe is the D-controller reacting to the noise of the IR sensor. However great a D-controller may seem at stabilising a system, this is only true on paper. Ultimately, the use of derivative action can be beneficial, but it has to be used in the right situations and in the right amounts. Your starting assumption should be to see if the process will run satisfactorily on PI control alone. Adding derivative should be done cautiously and with appropriate filtering of the signal.  
	\item Lowering the derivative filter gain to $K_F = 0.5$ makes the system more stable because the sensor's noise is filtered more (derivative filter time constant is lowered to 2~s). Increasing the derivative filter gain to $K_F = 2$ makes the system less stable.
\end{enumerate}

\subsection*{Excercise 3.13}
\begin{enumerate}
	\setlength\itemsep{0em}
	\item Added dead time destabilises the closed-loop system.
\end{enumerate}

\subsection*{Excercise 3.14}
\begin{enumerate}
	\setlength\itemsep{0em}
	\item The magnitude of the amplitude is close to zero, the signals are out of phase.
	\item The magnitude of the amplitude is close to one, the signals are out of phase.
	\item The magnitude of the amplitude is higher than one, the signals are shifted by roughly 90 degrees.
	\item The magnitude of the ampltiude is close to one, the signals are in phase.
	\item The approximate Bode diagram is characteristic of a second-order system (Fig.~\ref{fig:approx_bode_diagram_closed}).
\end{enumerate}
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

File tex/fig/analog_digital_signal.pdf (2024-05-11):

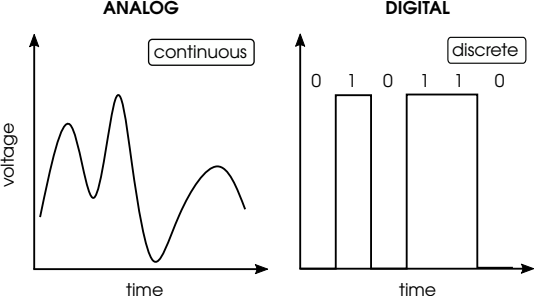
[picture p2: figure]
time; voltage; ANALOG; DIGITAL; continuous; discrete

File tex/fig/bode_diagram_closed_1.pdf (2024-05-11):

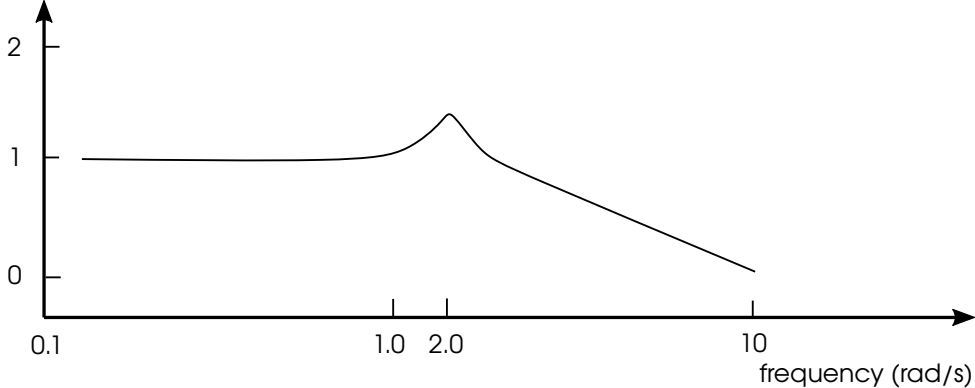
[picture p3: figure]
frequency (rad/s)

Magnitude (-)

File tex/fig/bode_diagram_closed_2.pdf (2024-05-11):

Phase shift (deg.)

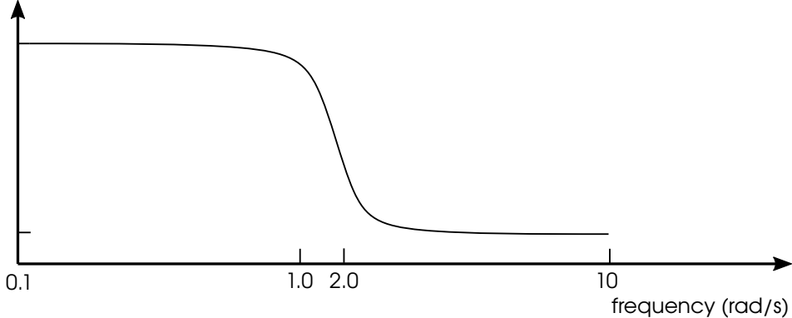
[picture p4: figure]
frequency (rad/s)

-1800

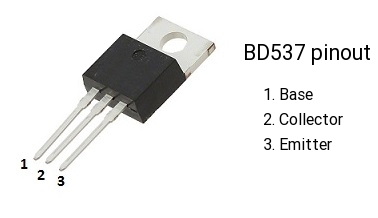
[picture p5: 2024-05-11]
tex/fig/BD537.jpg

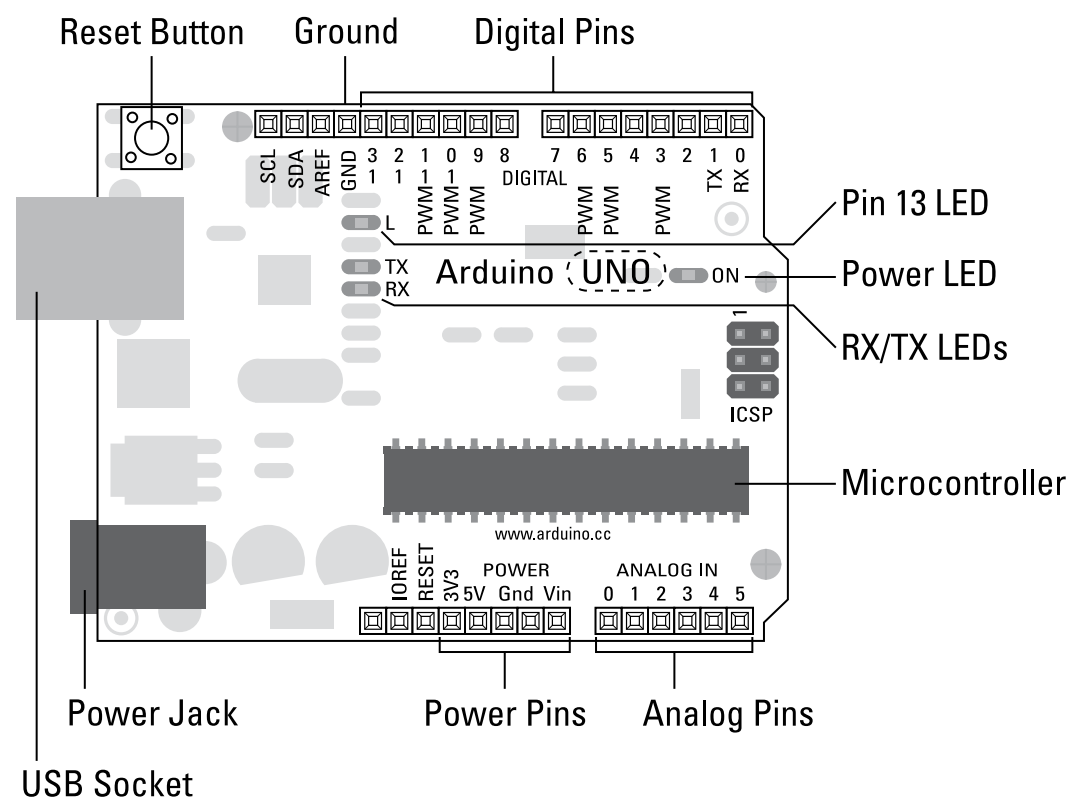
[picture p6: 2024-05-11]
tex/fig/ARDUINO_UNO2png.png

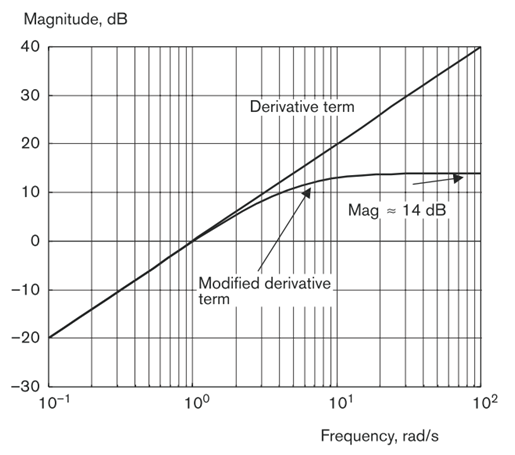
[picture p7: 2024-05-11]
tex/fig/bode_mD.png

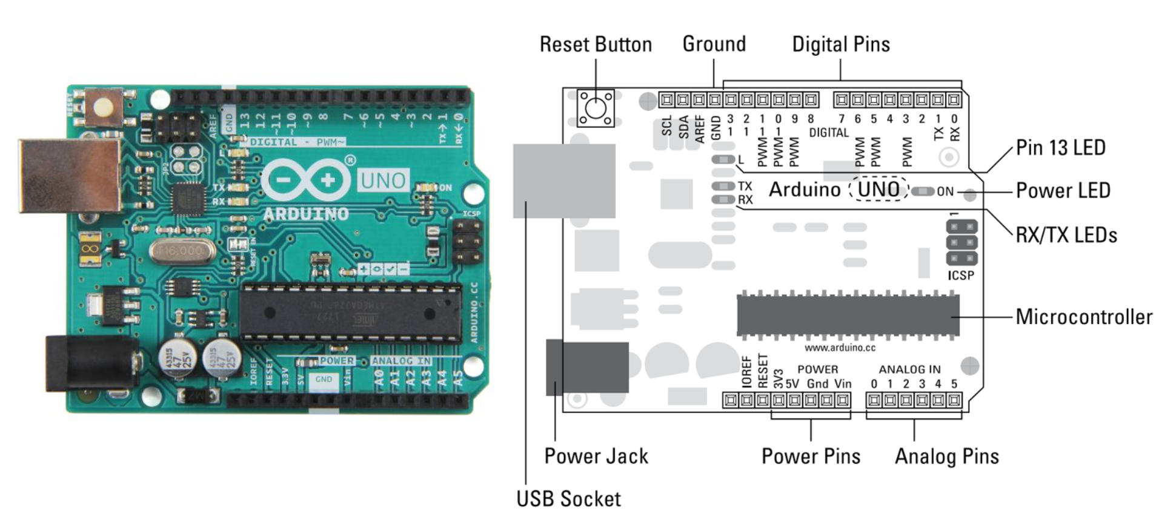
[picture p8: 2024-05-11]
tex/fig/ARDUINO_UNO.png

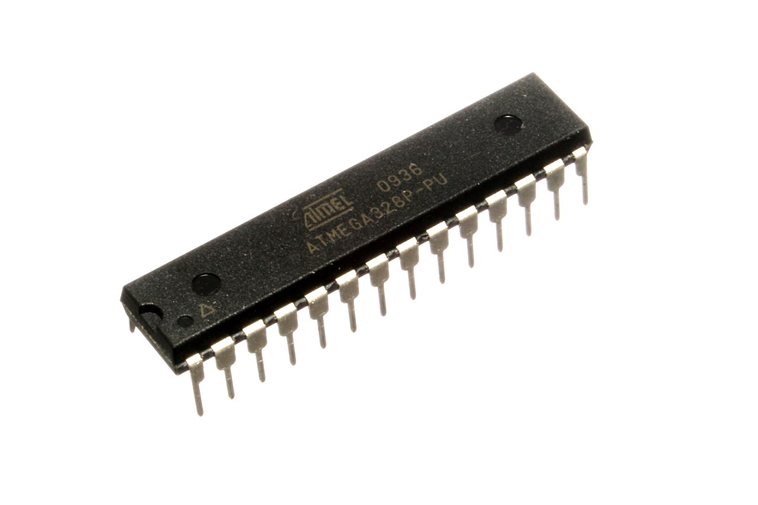
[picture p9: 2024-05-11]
tex/fig/ATmega328.jpg

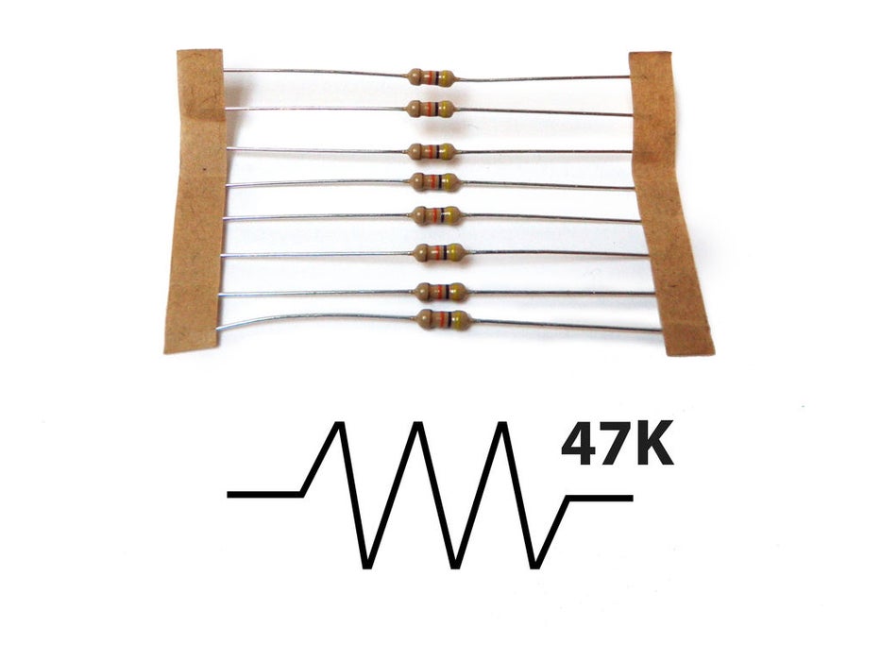
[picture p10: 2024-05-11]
tex/fig/resistor.jpg

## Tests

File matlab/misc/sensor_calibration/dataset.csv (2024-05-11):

height | voltage
0.37 | 1.25
0.39 | 1.4
0.4 | 1.45
0.35 | 1.2
0.38 | 1.3
0.34 | 1.15
0.33 | 1.05
0.31 | 1
0.34 | 1.1
0.27 | 0.95
0.25 | 0.9
0.16 | 0.82
0.2 | 0.85
0.14 | 0.79
0.1 | 0.77
0.12 | 0.78
0.15 | 0.8
0.05 | 0.74
0.06 | 0.75
0 | 0.72
0.41 | 1.5
0.42 | 1.6
0.425 | 1.625
0.45 | 1.9
0.44 | 1.78
0.465 | 2
0.525 | 2.05
0.57 | 2.55
0.49 | 1.95
0.47 | 2
0.59 | 2.9
0.55 | 2.35

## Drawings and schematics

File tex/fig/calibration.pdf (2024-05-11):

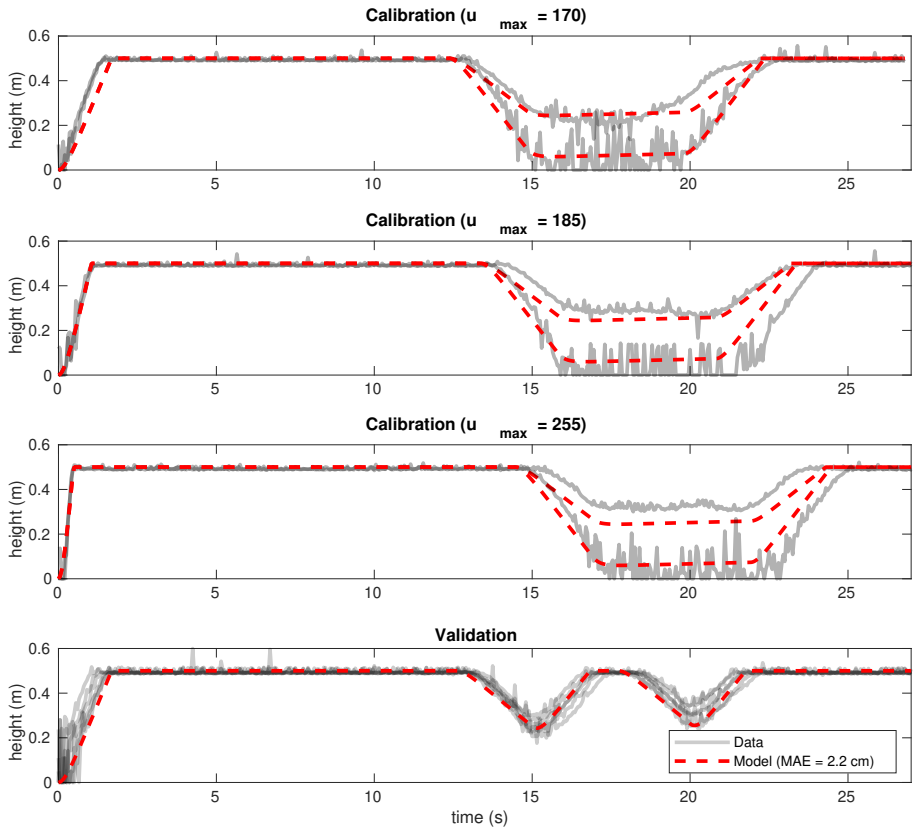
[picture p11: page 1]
height (m); Calibration (u; max = 170); max = 185); max = 255); time (s); Validation

Data
Model (MAE = 2.2 cm)

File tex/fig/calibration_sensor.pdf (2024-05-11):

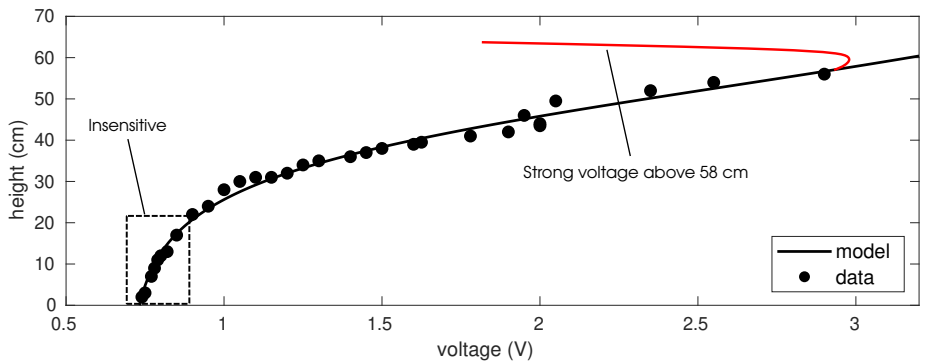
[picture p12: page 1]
voltage (V); height (cm); model data; Insensitive

Strong voltage above 58 cm

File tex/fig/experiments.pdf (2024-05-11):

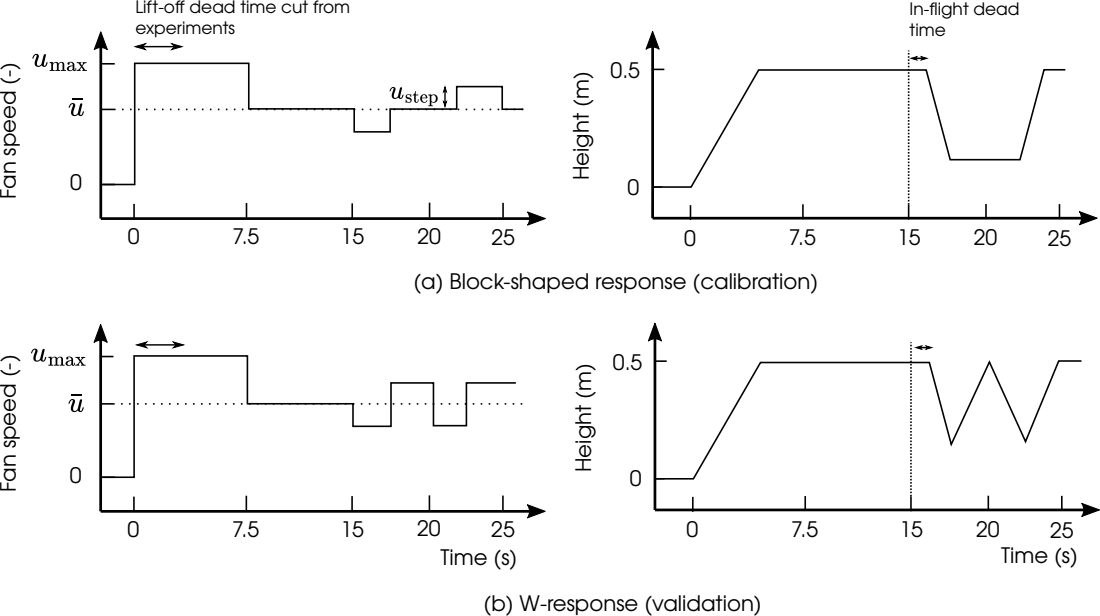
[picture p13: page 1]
Fan speed (-); Height (m); Time (s); (b) W-response (validation)

Lift-off dead time cut from
experiments

In-flight dead
time

(a) Block-shaped response (calibration)

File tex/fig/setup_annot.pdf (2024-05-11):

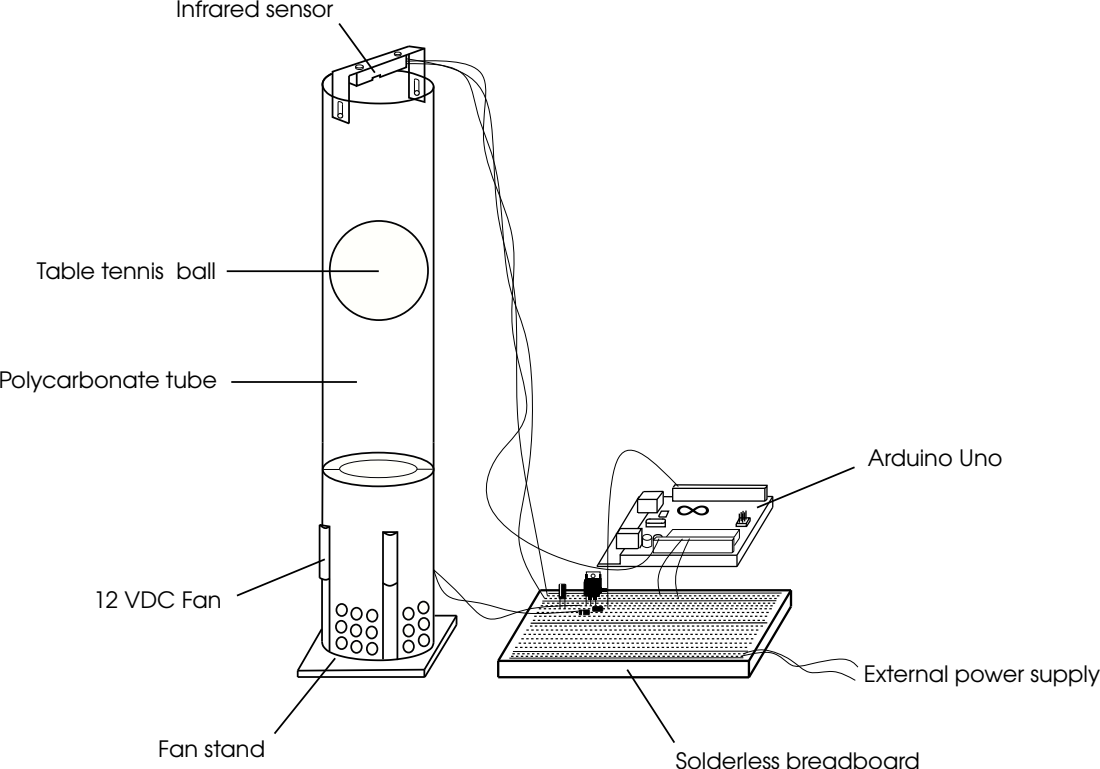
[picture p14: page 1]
Infrared sensor; Polycarbonate tube; 12 VDC Fan; Fan stand; Solderless breadboard; Arduino Uno

Table tennis ball

External power supply

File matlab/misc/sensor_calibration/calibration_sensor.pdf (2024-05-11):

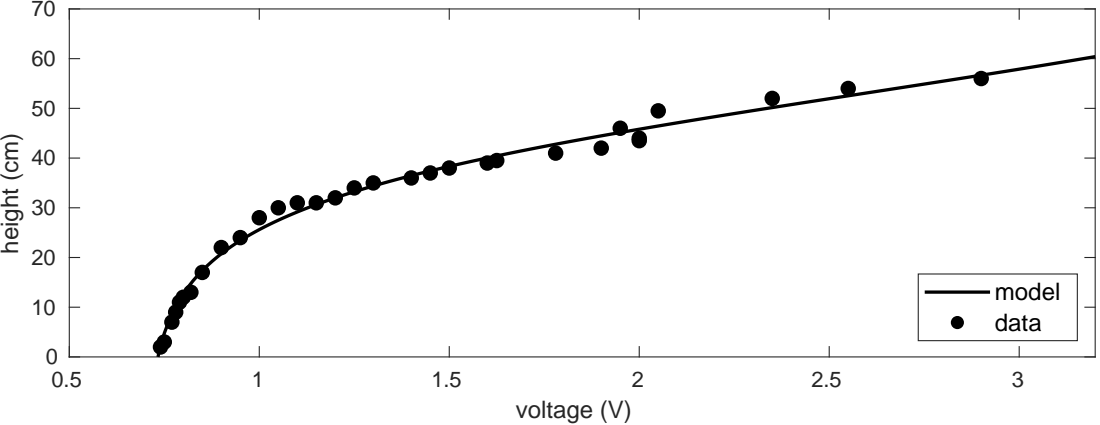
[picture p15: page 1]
voltage (V); height (cm); model data

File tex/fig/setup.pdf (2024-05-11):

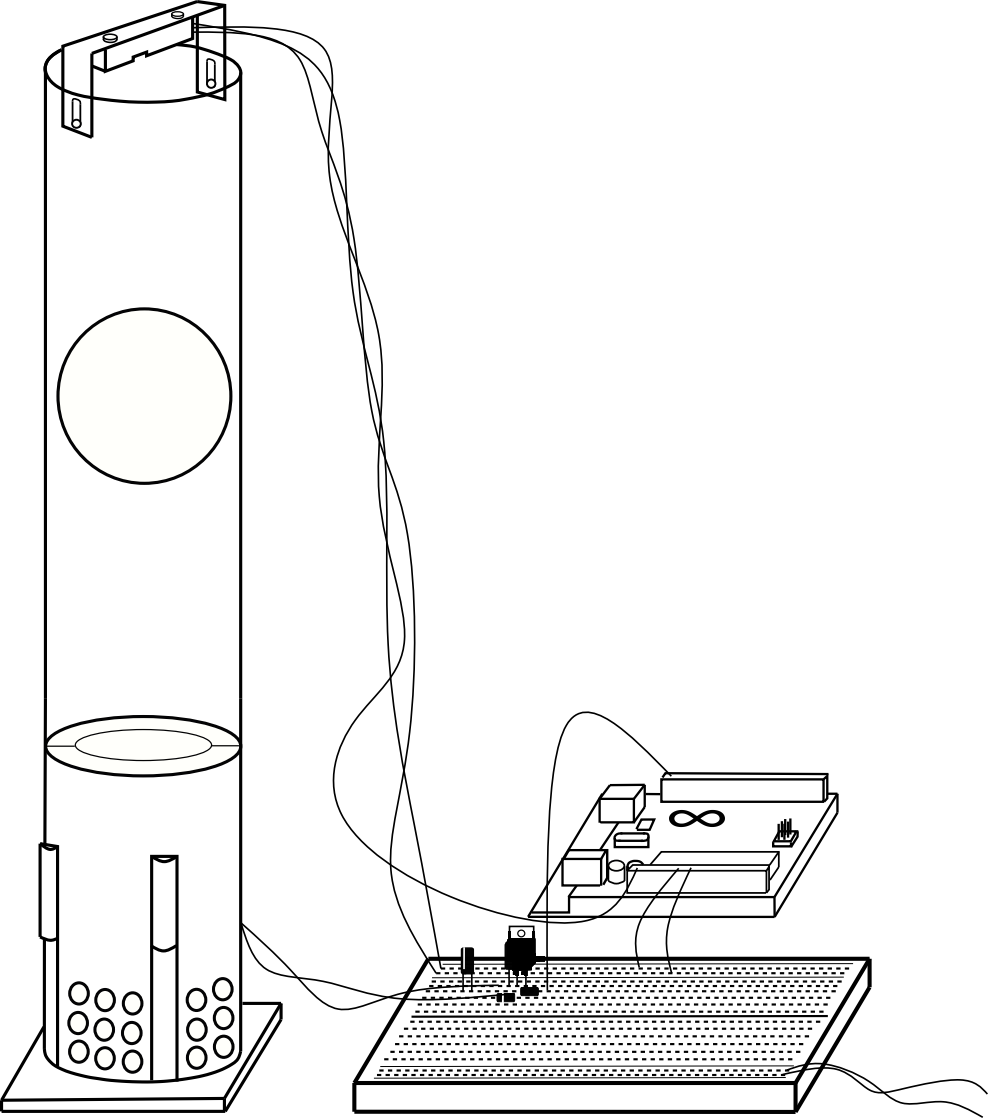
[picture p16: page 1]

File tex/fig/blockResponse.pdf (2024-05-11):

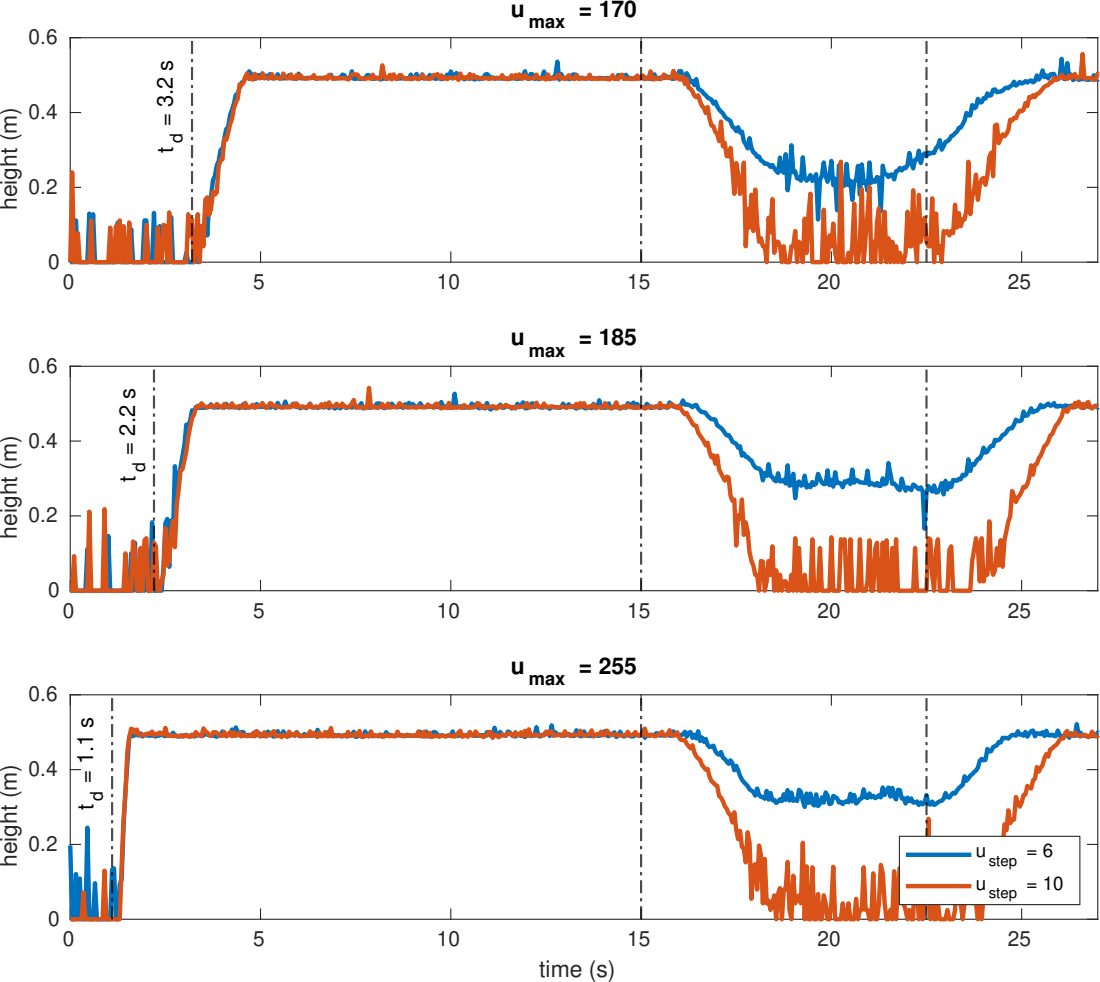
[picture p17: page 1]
height (m); max; time (s); ustep = 6 ustep = 10
